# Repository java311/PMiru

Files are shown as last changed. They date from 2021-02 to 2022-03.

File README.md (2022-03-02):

# P-MIRU
An Open Source hyperspectral polarized light camera. 



## System Description

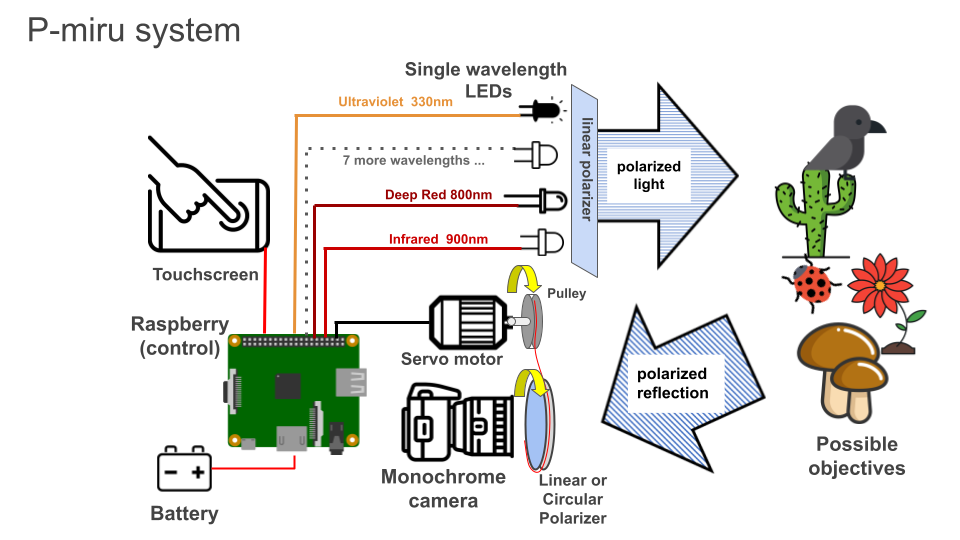
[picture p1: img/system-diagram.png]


Last Report: https://docs.google.com/presentation/d/1GZiw_HKL_oGRWR23fGHUSqiq1QuJ7bnZjt9xg0AGACE/edit?usp=sharing

## Actual hardware

### First prototype

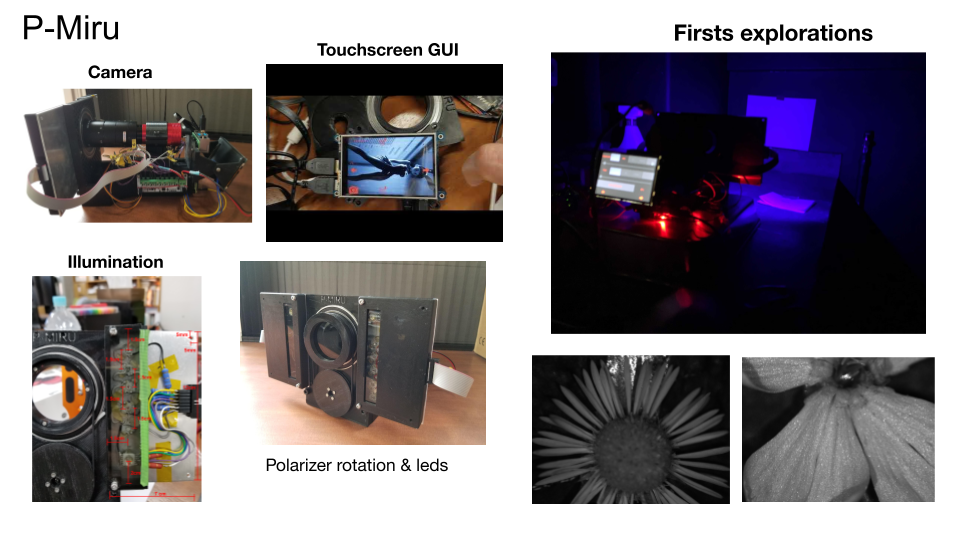
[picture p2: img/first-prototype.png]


### Last prototype

Front 
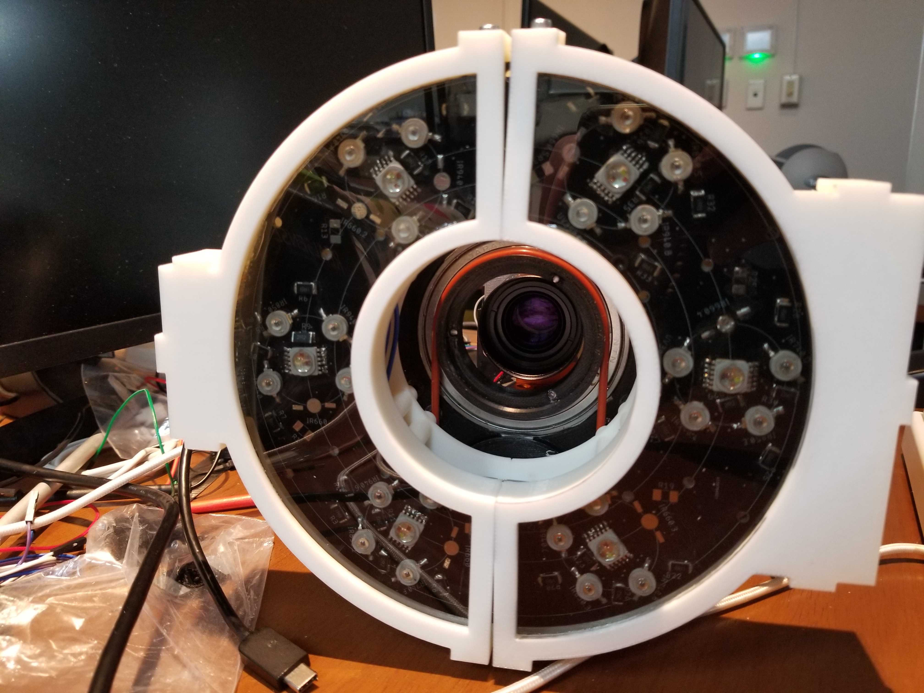
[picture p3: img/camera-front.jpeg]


Back
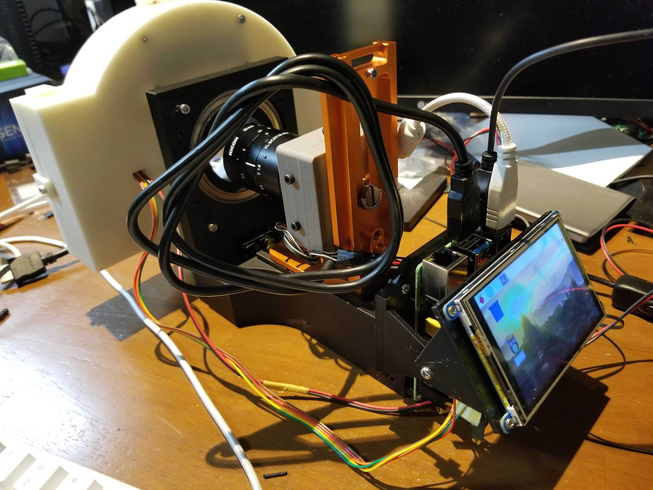
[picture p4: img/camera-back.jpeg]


## User Guide

#### **Turn ON and start the sofware**
To turn ON the camera you must use 2 power supplies. One for the Raspberry and othe other for the LEDs. 
So the transformer with the USB cable goes to the Raspberry. 
The other power supply must be connected to the first control board. This power supply is directly connected with cables.  

#### **Graphical User Interface**
The sofware has 3 diffrent screens.

**Camera screen**



This is the principal screen where you can take pictures and see the camera output. 

**Viewer screen**



In this screen you can navigate that the camera has taken

**Configuration screen**



In this screen, you can configure the Exposure and Gain values of the camera viewer. 
From here you can also execute the auto calibration, to normalize the exposure levels for all the light wavelenghts.

#### **Exposure levels calibration** 
The exposure and gain levels of the camera MUST be calibrated everytime the light conditions change. 
This is step is necessary in order to maintain the same ilumination level for all the illumination wavelenghts. 

To calibrate the exposure levels you need to the following: 
1. Put the camera inside a box, to block other light sources. 

2. Put a blank objective infront of the camera. For this, you can paste a white paper on side of the box the camera is looking. 

3. Turn ON the camera, open the software, go to the Configuration screen and click the "Auto Calibration" button. 

4. Then you have to wait between 10 to 15 minutes. The process takes a long time, please be patient. (you can see the progress of the task next to the "Auto Calibration" button) 

5. After this exposure and gain values of each color are automatically saved in the config.json file. So, this values can be used if the light conditions do not change.  

#### **Use the camera with monitor, keyboard and mouse**
Sometimes is easier to operate the camera with monitor, keyboard and mouse. Just like a PC. 
To do so, BEFORE turning on the camera, connect the monitor using mini HMDI cable. Also connect
a keyboard and mouse to the USB ports. 

( Note. Bluethooth mouse and keyboard are NOT recommended. To many periferals connected to the Raspberry will cause power supply failures, like: slow wifi, slow processor, camera failure.)

Then you have to:

1. Disable the touchscreen input
Then you have to disable the touch commands of the touchscreen. To do so edit the Kivy's config file located in: `/home/pi/PMiru/.kivy/config.ini`. For this you can open the Text Editor from `Menu.. Accesories... Text Editor`. Then find the lines responsible for touch and add a `#` at the beginning to comment them. 
```
[input]
mouse = mouse
#Touchscreen function for 270 degrees orientation
#mtdev_%(name)s = probesysfs,provider=mtdev
#hid_%(name)s = probesysfs,provider=hidinput,param=rotation=270,param=invert_y=1
```
Then save the changes and reboot.

2. Fix the screen orientation
If the image in the monitor is upside down. To flip the image you need to reconfigure the Raspberry monitor output by executing the following commands: 
```
cd /home/pi/
cd Raspberry-Pi-Installer-Scripts
sudo python3 adafruit-pitft.py
```

This will run the touchscreen configuration script. With the keyboard select the following options:
```
[4] [90 degrees] [No] [Yes] and then reboot. 
```
After the reboot the screen in the monitor should be correct. But the image in the touchscreen will be upsidedown. 

#### **Use the camera with touch screen only** 
If you want to use the camera with touchscreen. You must:
1. Enable the touchscreen input
To enable the touch commands of the touchscreen. To do so edit the Kivy's config file located in: `/home/pi/PMiru/.kivy/config.ini`. For this you can open the Text Editor from `Menu.. Accesories... Text Editor`. Then find the lines responsible for touch and erase the `#` at the beginning to uncomment them. 
```
[input]
mouse = mouse
#Touchscreen function for 270 degrees orientation
mtdev_%(name)s = probesysfs,provider=mtdev
hid_%(name)s = probesysfs,provider=hidinput,param=rotation=270,param=invert_y=1
```

2. Fix the screen orientation
If the image in the monitor is upside down. To flip the image you need to reconfigure the Raspberry monitor output by executing the following commands: 
```
cd /home/pi/
cd Raspberry-Pi-Installer-Scripts
sudo python3 adafruit-pitft.py
```

This will run the touchscreen configuration script. With the keyboard select the following options:
```
[4] [270 degrees] [No] [Yes] and then reboot. 
```
After the reboot the screen in the touchscreen should be correct but in the monitor it will be upsidedown. 

#### How to transfer the photos to my PC ?
1. The easiest way is to connect a USB thumbdrive or harddrive to the Raspberry. Then use 
Raspberry file explorer to copy the files from `/home/pi/PMiru/captures` to your external USB drive. 

2. The second method is to copy the files direclty from the SD card. 
Take the SD card from the bottom of the Raspberry PI and insert in your PC.

In Windows you can use Ext2explore ( https://sourceforge.net/projects/ext2read/files/Ext2read%20Version%202.2%20%28Latest%29/ ) to navigate SD card 
and copy the pictures from `/home/pi/PMiru/captures` to your PC. 

### How to update P-Miru from github
The easiest way to update P-Miru software is to do it from the github repository: `https://github.com/java311/PMiru`.

To do it you must open a terminal and type the following commands:
```
cd /home/pi/PMiru
git checkout
git pull origin master
```
Then you will be asked for a login and password. Ask the slack channel to get those.

### Factory Reset
A factory reset **erases all the files in the SD card** and installs PMiru Raspberry image.

1. For this you need to download the **LAST** Raspberry PMiru image file from: 
https://drive.google.com/file/d/16q-wU4vT5028pIW1XGyObwF1UAekve8w/view?usp=sharing
(mirror)
https://mega.nz/file/wwF0jLZD#PZPAzkS5hg5-15VtYI9gsM4PogvQ8KutajpRCXCJKG8

2. Insert the SD-card of the camera and instert it into your PC.

3. Then Launch the **Raspberry Pi Imager**. You can download and install Raspberry Pi Imager from: https://www.raspberrypi.org/software/ 


4. Select **Use custom** from Choose OS menu. 



5. Select the image file you downloaded. 



6. Select the micro SD card you wish to burn it to. 



7. Click Write and wait. 



8. Once it finish put the SD card back to the camera's Raspberry.  

### How to connect the camera

#### **Touch Screen connections**
The touchscreen must be connected to the Raspberyy using SPI0, 3.3V, 5V, ground and plus touch communication pins.
Here are the PINs configuration: 

| PIN Function  | Raspbery-LCD PIN number |
| ------------- | ------------- |
| 5 Volt   | PIN 2  |
| 3.3 Volt   | PIN 1  |
| SPI0 and COMMs   | PINs 18, 19, 20, 21, 22, 23, 24, 26  |

LCD PIN numbers are the same as the Raspberry. 
Just check the orientation of the LCD PIN slot, it is designed to cover all the Raspberry output pins.



#### **LED PCB donut connections **
The PCB with the donut shape is controled with 2 Amperka boards. This is where the cables from the donut PCB are connected. Then, the boards need to be connected to the Raspberry PINs. 

The first control board must connected to the Raspberry using the following PINs: 
| Control Board IN  | Raspberry PINs |
| ------------- | ------------- |
| pulse icon pin   | PIN 40  (SLCK) |
| G (Ground) | PIN 39 (GND)  |
| DI   | PIN 38 (MOSI SPI1) |
| CS   | PIN 36 (SPI CE2) |
| pin between GND and Clock (5V)   | PIN 2 (5V) |

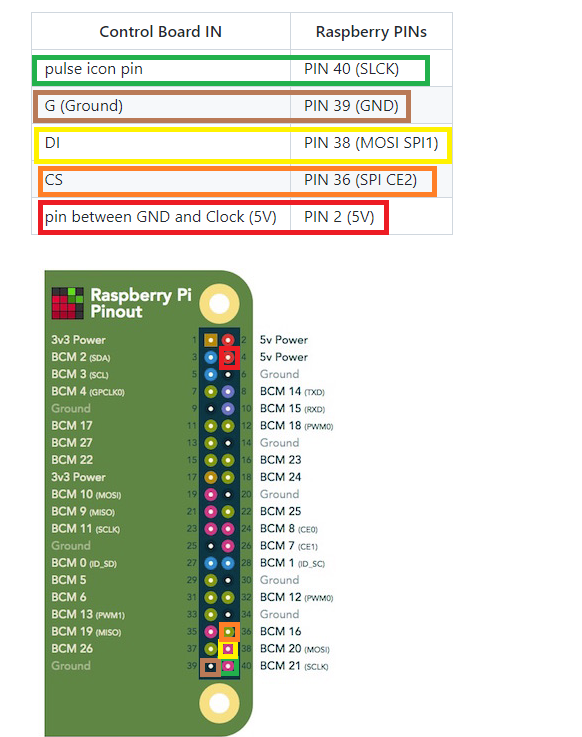
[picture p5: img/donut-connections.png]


Then the fist board OUT must connected the the second control board IN.
To connect them togheter, just connect the SPI OUT of the first board to the same PINS on the SPI IN pins of the second board. 

| First board OUT  | Second board IN |
| ------------- | ------------- |
| Pulse icon pin   | Pulse icon pin (SLCK) |
| G (Ground) | G (Ground)  |
| pin between GND and Clock (5V) | pin between GND and Clock (5V) |
| DI (MOSI) | DI (MOSI) |
| CS (CS)  | CS (CS) |

Inside the donut the LEDs can be connected in any other to the two boards. The order in which you want to controll then can be defined in the `config.json` file. 

#### **Motor connections**
The motor gets power from the second board, but it is controlled directly from the Raspberry. 
So, it must be connected the following way: 

| Motor  | Connection |
| ------------- | ------------- |
| 5 Volt   | Control board 2 PIN between CS and GND |
| Ground   | COntrol board 2 GND PIN |
| Comm    | Raspberry PIN 32 (PWM0)  |

#### **Camera connection**
The camera is connected using a USB 2 or USB 3 cable. 
Even your grandpa can do this...

### How to edit the config.json file 
TODO 

### Troubleshooting

#### **The software got freezed**
If the software got freezed for a very long time. You can close it by pressing Ctrl + C in the terminal window (The terminal window is the black screen that opens with P-Miru)

If you are just using the touch screen you can close the window by using Xkill. 
Xkill is an application that lets you "kill" or close any graphical app in Linux. 
Open it from, the main menu, others and Xkill. Then just click directly to PMiru screen. 

#### **The program freeze or stoped and the LEDs are ON**
Please DO NOT allow this to happen. This can harm the LEDs. To turn OFF the LEDs, just open P-Miru again and the LEDs will turn OFF. 

#### **The autocalibration gets stuck in a single LED for a long time ( more than 20 min)**
This means that the camera is not receving enough light from the LED. 
This happend frequenctly with the UV LED (320nm or LED #7). 

To solve the problem you must improve the light conditions in your setup. Maybe it would be necessary to approach the camera to the objective. 
Another solution, could be to avoid the usage of this light by editing Pmiru's `config.json` file.  

#### **When taking photos the progress bar restarts several times** 
That is normal. After all the photos are taking the camera also create the stacked tiff files for each wavelenght. 
This could take even longer than the capture process. If you do not want to use stacked tiff files, you can edit Pmiru's `config.json` file.

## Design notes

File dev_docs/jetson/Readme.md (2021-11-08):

# Install instructions for Jetson Nano

## Install general dependencies tools
```
install pip3
apt get install python3-pip

install cython
pip install -U cython 

install numpy and tifffile  (-U means --update)
pip3 install -U numpy 
pip3 install -U tifffile 
```

## OpenCV
Install Open CV using pip3, to avoid compiling source code. 

First install dependencies   

`pip3 install scikit-build`

Then install OpenCV using pip. 

`pip3 install opencv-python`

It is necessary to install contrib version for superpixel support
`pip3 install opencv-contrib-python`

Be patient this step takes a lot of time

Then install the OpenCV dependencies 
```
sudo apt-get install libatlas-base-dev
sudo apt-get install libhdf5-dev
sudo apt-get install libhdf5-serial-dev
sudo apt-get install libatlas-base-dev
sudo apt-get install libjasper-dev
sudo apt-get install libqtgui4 
sudo apt-get install libqt4-test
```

Also it is necessary to install polanalyser for the superpixel segmentation:
`pip install git+https://github.com/elerac/polanalyser`

## Kivy
The best is to install it from apt
https://kivy.org/doc/stable/installation/installation-linux.html#start-from-the-command-line

### SDL Kivy bug
There is a bug related do the SDL (https://github.com/kivy/kivy/issues/6007), that can only be fixed by installing an updated version of SDL by compiling the source code. Please follow this instructions: https://github.com/dhewm/dhewm3/issues/335#issuecomment-750332678

Once you have compiled SDL, you must link the compiled libraries by adding the following line to  `~/.bashrc` :

`export LD_LIBRARY_PATH=/home/pmiru/tmp/SDL2-2.0.8/build`

### Pillow Kivy bug 
Kivy has a problem when trying to render fonts uising Free Type fonts. To solve this problem, first install the free type development package:

`sudo apt-get install libfreetype6-dev`

Then reinstall Pillow 

```
$ sudo apt-get install libfreetype6-dev
$ pip uninstall pillow
$ pip install --no-cache-dir pillow
```

( Instructions taken from: https://stackoverflow.com/questions/4011705/python-the-imagingft-c-module-is-not-installed )

## Install ZWO libraries 
`pip3 install zwoasi`

Then it is necessary to install ASIO C++ binary library, from INDI-lib repositories (https://indilib.org/download.html):

```
sudo apt-add-repository ppa:mutlaqja/ppa
sudo apt-get update
sudo apt-get install indi-full gsc
```

## Install Octofet dependencies
```
pip3 install -U spidev
pip3 install -U pigpio
```

## Install jetston-GPIO libraries 
pigpio doesnt work in jetson nano, so it is necessary to use Jetson GPIO libraries insteadl 

`sudo pip install Jetson.GPIO`

Also follow the instructions of the git hub webpage (https://github.com/NVIDIA/jetson-gpio), because daemon and groups need further configuration

After this use Jetpack script to activate PWM and SPI pins 

`sudo /opt/nvidia/jetson-io/jetson-io.py`

To activate SPI is necessary to start the spidev kernel module automatically, by adding `spidev` it to the `/etc/modules` file.

## Connections

### How to connect the PWM

| Servo Motor PIN  | Jetson PIN  |
| ------------- | ------------- |
| 5 Volt   | PIN 4  |
| GND   | PIN 6  |
| COMM   | PIN 33  |

### Conenct Amperka boards

| Amperka  | Jetson PIN |
| ------------- | ------------- |
| pulse icon pin   | PIN 23  (SLCK) |
| G (Ground) | PIN 25 (GND)  |
| DI   | PIN 19 (MOSI SPI1) |
| CS   | PIN 24 (SPI CS0) |
| pin between GND and Clock (5V)   | PIN 2 (5V) |

#### LED connection troubleshoot
- Issue: Leds turn on at the same or in the wrong order
- Fix: It is caused by a missconnection of the CS cable on the wrong pin.

- Issue: Amperka LED do not turn on and also LEDs do not turn on
- Fix: The 5V from the Jetson board is not connected to Amperka board

- Issue: Amperka LED is ON but LEDs do not turn on
- Fix: The 3.3v power supply is not connected to the Amperka board

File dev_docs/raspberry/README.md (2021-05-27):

# P-MIRU
An Open Source hyperspectral polarized light camera. 



## Install instructions for Raspberry

These instructions are for a Raspberry fresh install. 

### Install Numpy and Tifffile
```
pip3 install numpy
pip3 install tifffile
```

### Install OpenCV 3
use pip3 (it MUST be pip3) as: 
`pip3 install opencv-python`

Then install all OpenCV dependencies:
```
sudo apt-get install libatlas-base-dev
sudo apt-get install libhdf5-dev
sudo apt-get install libhdf5-serial-dev
sudo apt-get install libatlas-base-dev
sudo apt-get install libjasper-dev
sudo apt-get install libqtgui4 
sudo apt-get install libqt4-test
```

### Install Kivy
First install Kivy dependencies: 
`sudo apt install libsdl2-dev libsdl2-image-dev libsdl2-mixer-dev libsdl2-ttf-dev`
then install kivy using pip3 
`python3 -m pip install kivy[base] `

Add the following to `~/.bashrc` to disable Kivy default arguments:
```
# disable kivy command line for pmiru
KIVY_NO_ARGS=1
export KIVY_NO_ARGS
```

### Install ZWO libraries
`pip3 install zwoasi`

Then it is necessary to install ASIO C++ binary library, from Astroberry PI repositories:
```
wget -O - https://www.astroberry.io/repo/key | sudo apt-key add -
sudo su -c "echo 'deb https://www.astroberry.io/repo/ buster main' > /etc/apt/sources.list.d/astroberry.list"
sudo apt update
sudo apt upgrade
sudo apt-get install indi-full
```

### Install NeoApi (Baumer) 
Neoapi is installed by downloading the WHL python packages from Baumer site: 
https://www.baumer.com/us/en/product-overview/industrial-cameras-image-processing/software/baumer-neoapi/c/42528

Download Baumer neoAPI Python v1.0 (Linux ARM)  (armhf, tar.gz option)

Then install the whl file accordingly to your python3 version:
```
python3 --version
python3 -m pip install neoapi-1.0.0-py[your python version]-none-any.whl
```

Also it is necessary to increase the USB cache size of Raspberry. To do so add this line to `/etc/rc.local`. Before the `exit 0`, add this: 
```
sudo sh -c 'echo 1024 > /sys/module/usbcore/parameters/usbfs_memory_mb' &
```

### Touch Screen Install
These are the instructions for the touch screen install
Use the following comands:  (taken from: https://learn.adafruit.com/adafruit-pitft-3-dot-5-touch-screen-for-raspberry-pi/easy-install-2 )
```
cd ~
sudo pip3 install --upgrade adafruit-python-shell click==7.0
git clone https://github.com/adafruit/Raspberry-Pi-Installer-Scripts.git
cd Raspberry-Pi-Installer-Scripts
```

Run Adafruit configuration script, with:
`sudo python3 adafruit-pitft.py `
and select the following options:
[4] [90 degrees] [No] [Yes] and DO NOT reboot. 

Also, Kivy needs special instructions to control the touch screen. 
Edit `~/.kivy/config.ini` and add the following lines in the [input] section:
```
[input]
mouse = mouse
mtdev_%(name)s = probesysfs,provider=mtdev
hid_%(name)s = probesysfs,provider=hidinput,param=rotation=90,param=invert_y=1
```

(NOTE: the rotation of the screen must be the same as indicated in Raspbery script) 

Also in the `[graphics]` section modify width and height parameters to 320, 240 respectevely.
And then Reboot

(NOTE: If you are going to use the camera without the touch screen, with mouse and keyboard.
Then the last two must be commented. Otherwise, Kivy will register ghost and random clicks. )

#### Touchscreen connection pins
The touchscreen must be connected to the Raspberyy using SPI0, 3.3V, 5V, Ground and 2 communications PINS 
Here are the PINs configuration: 

| PIN Function  | Raspbery-LCD PIN number |
| ------------- | ------------- |
| 5 Volt   | PIN 2  |
| 3.3 Volt   | PIN 1  |
| SPI0 and COMMs   | PINs 18, 19, 20, 21, 22, 23, 24, 26  |

LCD PIN numbers are the same as the Raspberry. 
Just check the orientation of the LCD PIN slot, it is designed to cover all the Raspberry output pins.



### Amperka board install (light control)
(Amperka python libraries were modified, so these are include in source code. There is no need to install them)
Since we are using SPI0 for the touchscreen, the light control boards must be connected using SPI1. 
First it is necesasry to enable SPI interface using sudo raspi-config. Then after reboot it is necessary
to enable SP1 too by editing `/boot/config.txt` and add the follwoing line:

`dtoverlay=spi1-3cs`

And then reboot. 
To check if SPI is activated excecute: `ls /dev/spi*`. The command output must be: 
```
pi@raspberrypi:~/PMiru $ ls /dev/spi*
/dev/spidev1.0  /dev/spidev1.1  /dev/spidev1.2
```

#### Amperka boards connection pins
Then connect Amperka board #0 with the Raspberry using the following PIN configuration: 
| Amperka  | Raspberry PIN |
| ------------- | ------------- |
| pulse icon pin   | PIN 40  (SLCK) |
| G (Ground) | PIN 39 (GND)  |
| DI   | PIN 38 (MOSI SPI1) |
| CS   | PIN 36 (SPI CE2) |
| pin between GND and Clock (5V)   | PIN 2 (5V) |



(The boards had been hacked to work with 3.3Volts 
with the cables soldered on each of the boards. Do not dissconnect them ! ) 

To control the 10 colors, it is necessary to have 2 Amperka boards connected to each other using SPI.
To connect them togheter, use jumper cables to connect the SPI output of board #0 to the same PINS of the SPI input in board #1
Connect all the 6 pins of SPI-Out (board #0) to the SPI-In (board #1) 

### Motor (PWM daemon) 
Motors are controlled using PWM. pigpio demon needs to be started as a daemon on every boot. 
To do so, use the following commands:
```
$ sudo systemctl enable pigpiod.service
$ sudo shutdown -r now
```
Then check if everything is OK by using 
`$ sudo systemctl status pigpiod.service`

Motor PINs are connected as follows: 
| Motor  | Amperka Board #2 |
| ------------- | ------------- |
| 5 Volt   | Amperka OUT between CS and GND |
| Ground   | Amperka OUT GND       PIN 39  |
| Comm    | Raspberry PIN 32 (PWM0)  |

### Finally 
Go to the folder where P-Miru is and excecute it using this command: 
`python3 pmiru.py -m` to star it maximized or without options for normal startup

### Optional
Set python3 as default (so when you call python you call python3 instead of python2)
https://linuxconfig.org/how-to-change-from-default-to-alternative-python-version-on-debian-linux

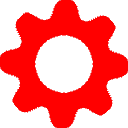
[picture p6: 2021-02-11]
config_red.png

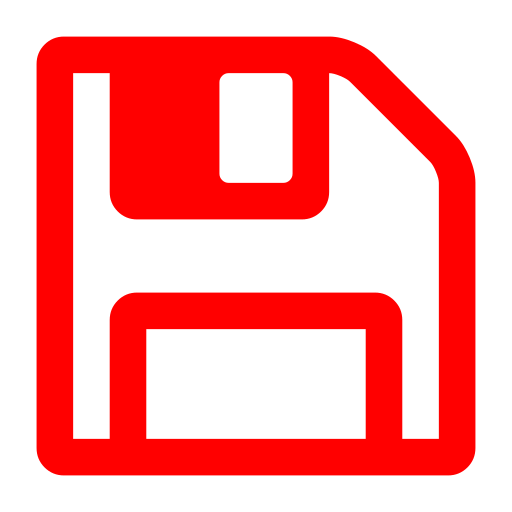
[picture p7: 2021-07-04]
save_red.png

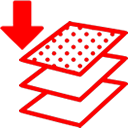
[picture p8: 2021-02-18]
layers_red_down.png

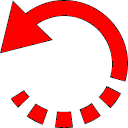
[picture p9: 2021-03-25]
rotate_left_red.png

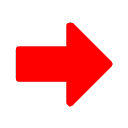
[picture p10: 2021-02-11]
right_red.png

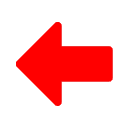
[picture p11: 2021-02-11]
left_red.png

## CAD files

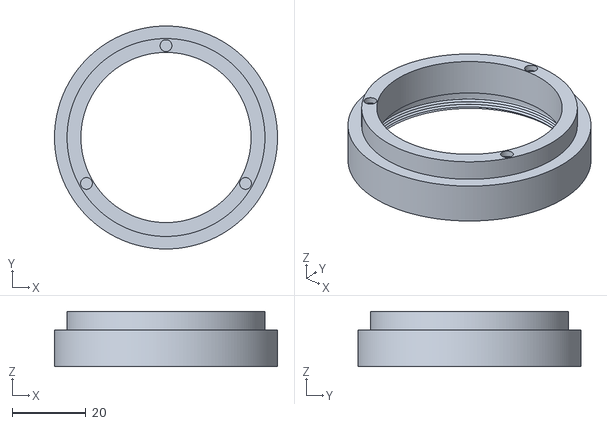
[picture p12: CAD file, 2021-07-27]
models/filter-rotation/PL servo rotator RS204MD FILTER HOLDER V26.stl
60.3 x 60.3 x 15.0

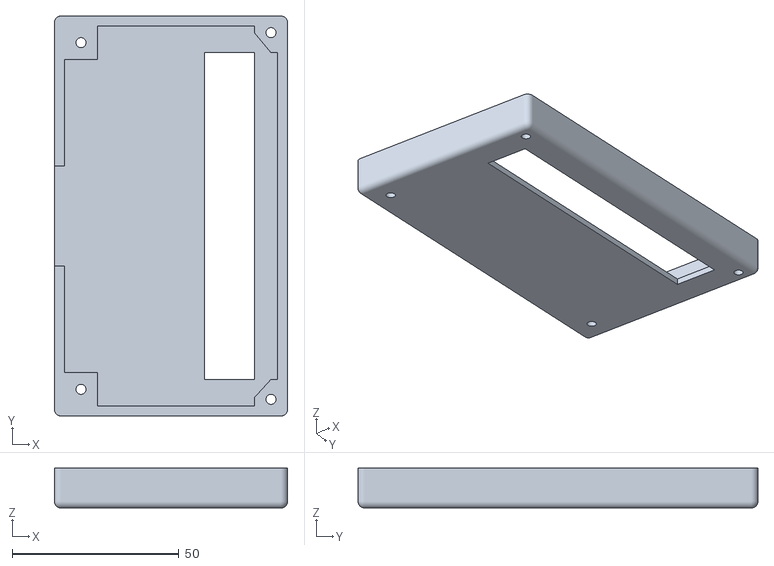
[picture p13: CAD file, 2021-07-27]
models/led-covers/LED window v2.stl
70.0 x 120.0 x 12.0

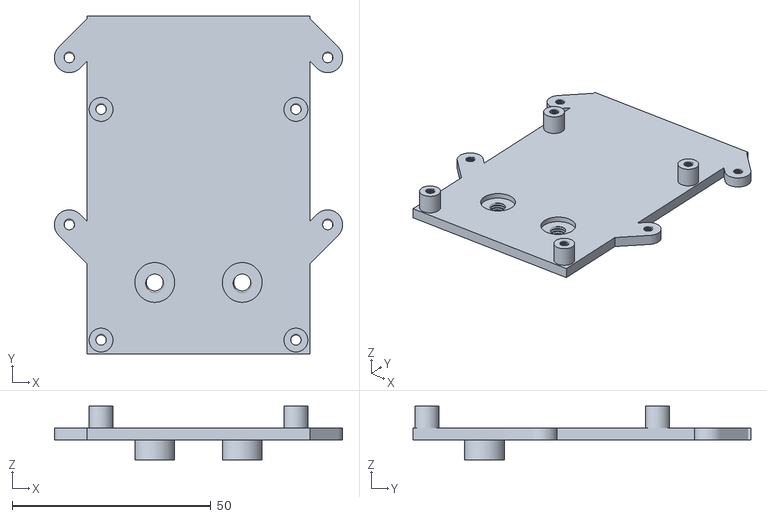
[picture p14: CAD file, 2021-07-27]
models/raspberry-stand/rasp_base.stl
72.5 x 85.0 x 13.5

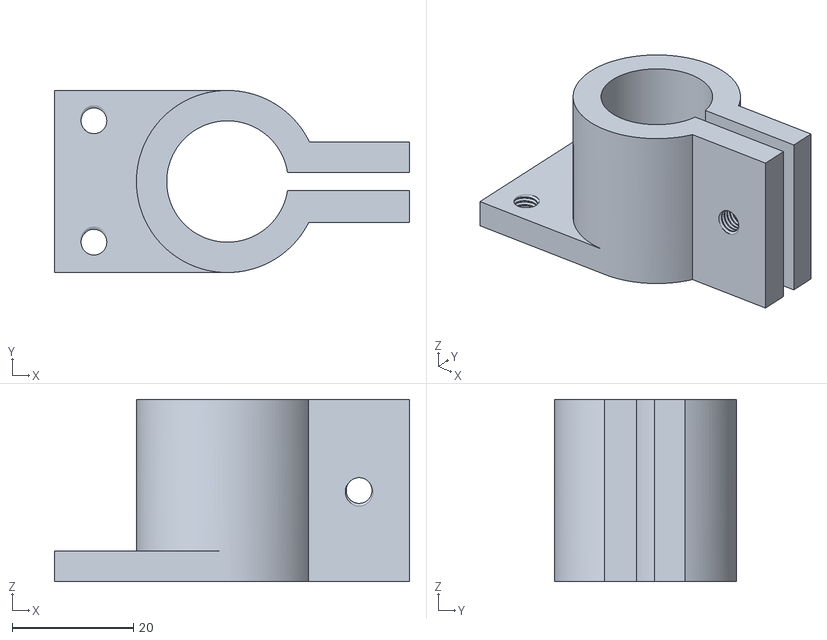
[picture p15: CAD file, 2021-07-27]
models/zwo-mini-camera-stand/zwo_mini_2nd_stand DOWN.stl
58.5 x 30.0 x 30.0

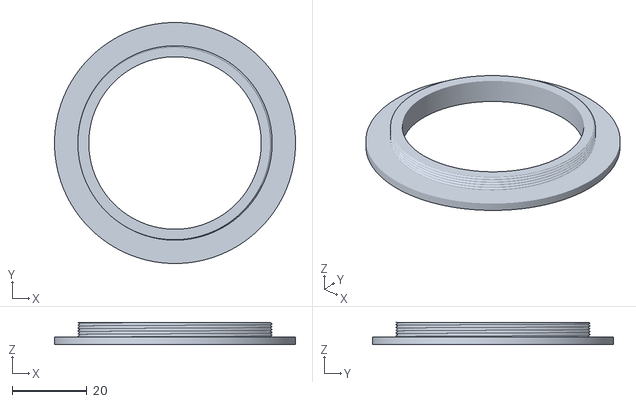
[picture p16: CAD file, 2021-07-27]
models/filter-rotation/PL servo rotator RS204MD FILTER HOLDER LID V24.stl
64.3 x 64.3 x 6.00

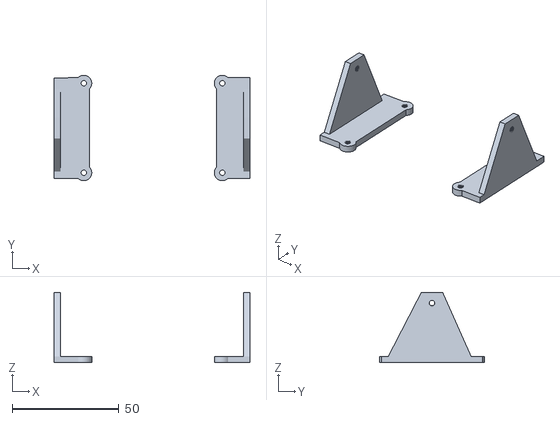
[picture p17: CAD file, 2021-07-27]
models/raspberry-stand/stands.stl
92.0 x 49.5 x 33.0

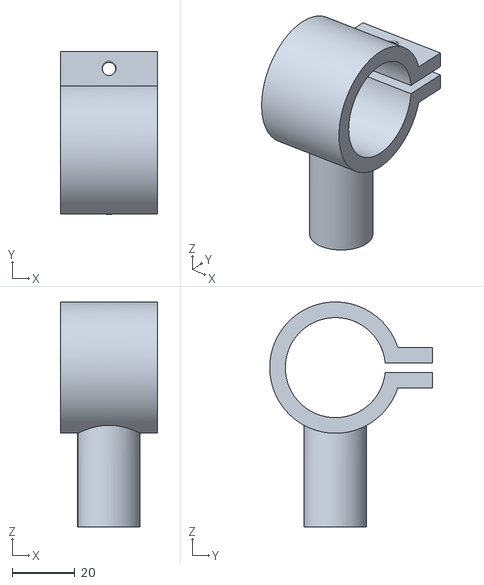
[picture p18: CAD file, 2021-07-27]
models/zwo-mini-camera-stand/zwo_mini_2nd_stand TOP.stl
31.0 x 52.0 x 72.0

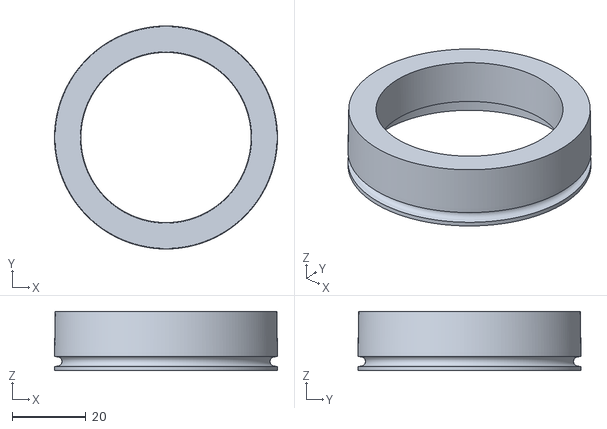
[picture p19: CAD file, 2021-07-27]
models/filter-rotation/PL servo rotator RS204MDBEARING PULLY V24.stl
60.3 x 60.3 x 16.0

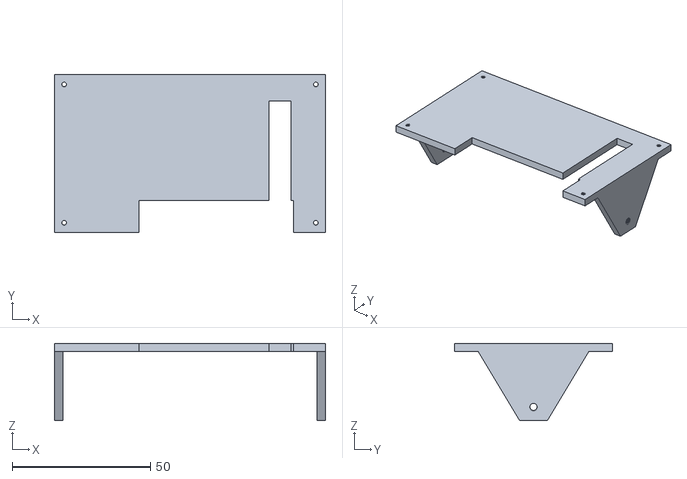
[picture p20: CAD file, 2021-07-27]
models/raspberry-stand/lcd base.stl
98.0 x 57.0 x 28.0

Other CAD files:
models/filter-rotation/PL servo rotator RS204MD v2.f3z

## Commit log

2021-03-05 baumer camera exposure, gain, capture and fix layers finished
2021-03-15 led control first commit. This needs more work
2021-03-22 add motor control, takehypercube modded, amperka libs included
2021-03-24 takehypercube bugfix, exit icon, motor class changes
2021-03-25 rotation button, takehyperspectral bugfix, update motorControl
2021-04-06 camera gui refresh, progress bar, led button,
2021-04-07 tiff stack by LED color and readme update
2021-04-08 camera sync bug fix, new light routines
2021-04-09 16 bit tiff file format change and camera visualization optimization
2021-04-12 partial commit of auto light calibration
2021-04-19 Exp and Gain calibration using LED lights with median stabilization
2021-04-22 missing file from the LED exp gain calibration previous push
2021-04-23 optimization for gain/exp led auto calibration
2021-05-05 baumer exp/gain calibration and takehypercube functions
2021-05-14 feature: motor angles from JSON file
2021-05-14 bugfix: camera viewer rotation for ZWO cameras
2021-07-04 feature: motor init calibration bugfix:zwomini exposure bugfix (not fully tested)
2021-07-23 feature: stop angle for the motor in config file. bugfix: angle names fix
2021-07-27 uploading models, polarizer rings are pulley missing.
    [LED window v2.stl, lcd base.stl, rasp_base.stl, stands.stl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]
2021-07-27 hotfix: motor name format +90 degrees
2021-07-27 hotfix: motor format name +90
2021-07-27 feature: polarizer ring and motor mount models added
    [PL servo rotator RS204MD FILTER HOLDER LID V24.stl, PL servo rotator RS204MD FILTER HOLDER V26.stl, PL servo rotator RS204MDBEARING PULLY V24.stl]
2021-10-16 bugfix: raspberry ledcontrol platform fix
2021-12-15 feature: support to elp chinese camera. (not finished yet, but works)
2022-01-31 adding servo rotator Fusion file
    [PL servo rotator RS204MD v2.f3z]
2022-01-31 feature:JSON config file change for LED donut
2022-01-31 bugfix:config channel/device hotfix
2022-11-18 [bugfix] yellow LED incorrectly labeled.
